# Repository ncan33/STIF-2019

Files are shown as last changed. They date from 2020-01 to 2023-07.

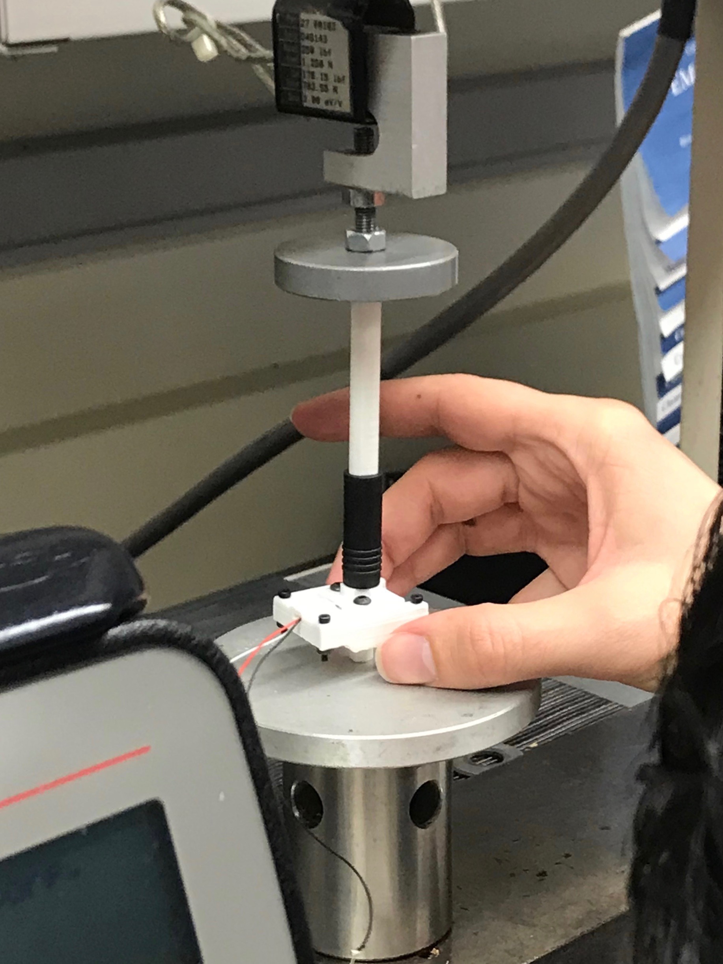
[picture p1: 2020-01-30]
data_analysis/images/calibration_on_MTS_machine.jpg

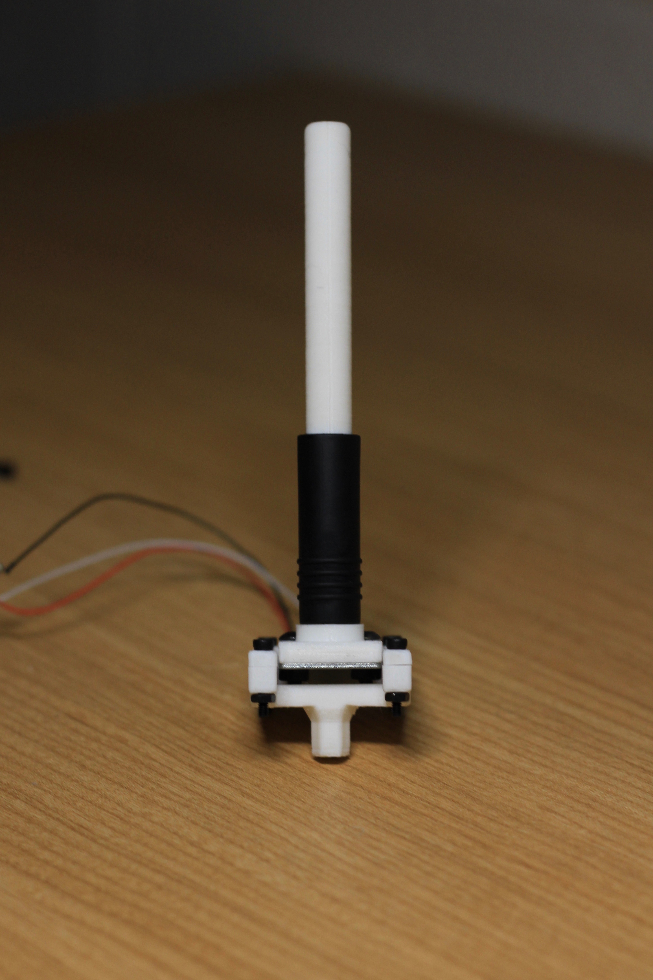
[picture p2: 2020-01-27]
visuals/IMG_4286.jpg

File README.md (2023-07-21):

# Surgery Tool with Integrated Force-gauge
This device measures the amount of force applied during controlled injury on mice. The CAD files for the 3D printed parts can be modified to achieve applicability for various surgery methods.

The strain of the aluminum beam inside the device is measured with two strain gauges. Arduino was used to control the electronics and translate incoming data from the strain gauge. Since strain is linearly correlated with the amount of force applied, the device can measure the applied force.

**[See Technical Report](https://github.com/ncan33/STIF-2019/blob/master/report.pdf)**

## Instructions
Download the Arduino IDE for Unix or Windows. In the Arduino IDE, install the [HX711 Ardunio Library](https://www.arduino.cc/reference/en/libraries/hx711-arduino-library/). Go to the `arduino_code/` and read the README. Then, go to the `arduino_code/final_code_STIF/` folder and read that README as well. Download `final_code_STIF.ino` on your computer and run it.

Our device at URMC has already been calibrated. For that specific device, you can find the digital output to force conversion in the technical report above (Equation 1). You will need to calibrate your own device, since each strain gauge is unique.

## Problem Scope
A method for measuring force values during controlled injury on mice was needed. Attempts to measure force through non-electronic means were made, however they were unsuccessful.

## Design Requirements
**Function**
* Needs to measure and store force data during surgery.
* Needs to act both as a force gauge _and_ the surgery tool.
* Will be operated by a human hand.
* Needs to measure up to 35 Newtons of force

**Reliability**
* Needs to be accurate up to research standards. The data collected by the device is intended to be published.
* Voltage output shall not be affected by ambient temperature.

**Dimensions**
* Needs to have an extruded part through which force will be applied on the mouse, which needs to satisfy the following constraints:
  * Regular hexagon
  * Short diagonal 6.15 mm
* The grip must be in the shape of the tool previously used to cause the controlled injury.

**Features**
* Must be easily operated without any special training.
* Must have an easy to use interface.
* Must have a tare function.
* Should be cleaned without damage to the device.

**Safety**
* Must not cause unwanted injuries to the mouse.
* Must not use dangerous voltages.
  
## Design Description
**Application:**
Check the [data_analysis folder](https://github.com/ncan33/STIF-2019/tree/master/data_analysis) for results acquired in the materials testing lab. An MTS machine was used to precisely apply known loads. Data collection was performed. Refer to [this document](https://github.com/ncan33/STIF-2019/blob/master/data_analysis/MATLAB_code_PDF/MTS_data_analysis_01_29_20.pdf) to access Force vs. Digital Output graph, and the 0.998 R-squared value. The graph is extremely linear and the device is proven to be functional with robust data. Repeated MTS test done for reliability-check yielded exactly the same results.

**Structure and Materials:**
All of the design requirements were met. 3D printed PLA comprises the structure of the tool due to its fine resolution and robust material properties. The strain gauge is integrated inside the surgical tool, and the device is multifunctional.

**Electronics:**
Arduino is used to control the electronics and translate incoming data from the strain gauges. The strain gauges are housed in a half-bridge load cell. Measurement range is between 0 to 98 Newtons. Measurement isn't affected by ambient temperature due to the half-bridge nature of the circuit. Two resistors were added to make a Wheatstone Bridge.

**Prototyping Cost:**
The total cost of the [materials](https://github.com/ncan33/DATAA-2019/tree/master/how_to_assemble#materials-and-tools) is under $75. Currently, 3D printing is commonly accesible at research facilities in developed countries. Thus, with the cost and tools taken into account, this is a device that is easy to assemble.

## Limitations and Future Improvements
_This project is still being developed. The first prototype is a success, however I have many ideas on how to improve it._

***Current works:***
* A housing for the electronic parts is being designed. It will be fabricated via 3D printing. I will post the .stl file in this repository.
* Means to update the strain gauge design is being researched.

***Limitations:***
* Can only measure up to 98 Newtons
* Can only be operated by a human
* Redesigning the device for other surgical applications would take hours of design and fabrication

***Future Improvements:***
* Easier adjustability
* Using a full bridge strain gauge
* Means to decrease noise in voltage detection by Arduino
* Improved grip
  * Can be made more ergonomic by allowing middle, ring, and pinky fingers to rest on an area
  * Silicon grip area is not secured to the grip
* Improved portability by removing the necessity of a computer
* Using a storage means different than the Arduino IDE serial monitor to collect data

## Creative Commons License
This device was designed, protoyped, fabricated, and assembled by Nejat Can. It is licensed under [CC Attribution-NonCommercial-ShareAlike 4.0](https://creativecommons.org/licenses/by-nc-sa/4.0/), so any research lab is allowed to use this repository to manufacture their own surgical force gauge.

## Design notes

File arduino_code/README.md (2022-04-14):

# READ THIS

***Main file*** `final_code_STIF.ino` ***uses both folders (*** `HX711_Arduino_Library` ***AND*** `final_code_STIF` ***) in order to work.***

The folder HX711_Arduino_Library needs to be placed in Arduino IDE's Library folder, or needs to be manually downloaded from the Arduino Libraries Manager located within the IDE.

`HX711_Arduino_Library` is taken from: https://github.com/bogde/HX711

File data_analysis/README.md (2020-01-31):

# DOCUMENT UNDER CONSTRUCTION

## Data Analysis
***Purpose***

***Procedure***

***Results***

The folder [CODE_MTS_test](https://github.com/ncan33/STIF-2019/blob/master/data_analysis/CODE_MTS_test/CODE_MTS_test.ino) has the

# Data Analysis
The folder [CODE_MTS_test](https://github.com/ncan33/STIF-2019/blob/master/data_analysis/CODE_MTS_test/CODE_MTS_test.ino) was the Arduino code used during the test. Data from the serial monitor was imported to Excel and raw data was analyzed in MATLAB. 

--

## Challenges
One encountered problem was the serial print had an unwanted string "Readings:". This made it harder to analyze in MATLAB, but the erase function was used to clear the cell array of unwanted strings. After the cell array was cleared of unwanted strings, it was converted to a matrix with double data type using the function str2num.

The easier approach would be to edit the Arduino code such that the 

NOT FINISHED

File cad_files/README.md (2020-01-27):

This device consists of three structural parts. STL files are to be sliced and 3D printed.

***Print these files***:
- ***[part1.stl](https://github.com/ncan33/DATAA-2019/blob/master/cad_files/DATAA_part1.stl)***
- ***[part2.stl](https://github.com/ncan33/DATAA-2019/blob/master/cad_files/DATAA_part2.stl)***
- ***[part3.stl](https://github.com/ncan33/DATAA-2019/blob/master/cad_files/DATAA_part3.stl)***

For instructions on how to manufacture and assemble the device, refer to the [how_to_assemble](https://github.com/ncan33/DATAA-2019/tree/master/how_to_assemble) folder.

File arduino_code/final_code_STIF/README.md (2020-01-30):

## Calibration
After the manufacturing & assembly process, the device must be calibrated otherwise the values will not be accurate.

**How to calibrate:**
1. Connect the Arduino to computer.
2. Apply a **known load** to the device (i.e. [perform a materials test](https://github.com/ncan33/STIF-2019/blob/master/visuals/calibration_on_MTS_machine.jpg) (recommended) or use a [precision scale](https://images-na.ssl-images-amazon.com/images/I/61YSVHc1hwL._SX425_.jpg) to apply measured loads).
3. Increase or decrease variable `calibration_factor` in the Arduino code. This will cause a direct change in the readings in the Serial Monitor.
4. When the readings match the known load, you've successfully calibrated the device.
5. (optional) Repeat with various loads ranging from 0-10.00 lb to check function.

## Tare
_The following is important. **The device is tared by resetting the Arduino**. IMPORTANT:_
* ***THE DEVICE MUST BE AT REST IN A VERTICAL POSITION WHEN THE CODE IS UPLOADED***
* ***THE DEVICE MUST BE AT REST IN A VERTICAL POSITION WHEN IT IS RESET***
* Ways to reset the device are:
  * Reupload the code, this will automatically restart the arduino
  * Hit the red reset button on the Arduino
  * Cut power supply to the Arduino, then reintroduce it
  
Tare before each usage. Tare more if needed throughout data collection.

## Measurement Unit
The measurement unit is user defined, and the default unit is pound-force.

_To define a new unit:_
1. Pick the desired force unit by editing the Arduino code
2. Recalibrate by following the steps of **How to calibrate** 

## Data Collection
To collect data, launch the Arduino IDE and connect the Arduino to your computer. Upload the code to your Arduino and open the Serial Monitor in the IDE.

## Research Application
The quality of the data is far more important for research application than convenience of usage. Therefore, for researchers the priority should be to collect good raw data, and perform data analysis afterwards. The following steps can be taken to ensure that the data is the high quality and easy to analyze using MATLAB or Excel.
* Remove units from serial output
* Use a lower calibration_factor (Recommended: 1000)
* Calibrate with a precision tool and collect multiple data points
* Refer to the [data_analysis](https://github.com/ncan33/STIF-2019/tree/master/data_analysis) for an example of data collection with this device and MATLAB analysis.
This repository has the code that satisfies these requirements. To access the code, refer to the folder [code_for_research_application](https://github.com/ncan33/STIF-2019/tree/master/arduino_code/code_for_research_application).

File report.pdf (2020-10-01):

# Device for Force Measurement in Non-Invasive Mouse ACL Injury Models: A Low-Cost and Portable Alternative

Nejat Can
Department of Biomedical Engineering University of Rochester
Rochester, NY, USA
ncan@u.rochester.edu

Abstract—Osteoarthritis and anterior cruciate ligament (ACL) injury have shown to be linked but poorly understood. Animal models are essential for understanding ACL injury, and there are a variety of models that have been developed. This study aims to introduce a new injury device that is significantly lower in cost and highly portable, suggesting ease of accessibility and better application for in situ studies. Computer-aided-design and 3D printing was used to precisely manufacture parts that encase an aluminum beam. The beam was fitted with a strain gauge, which was connected to a circuit that outputs a digital value proportional to strain. The relationship between the load on the beam and digital output was characterized by an experiment. The results indicated that digital output can confidently predict the load applied due to a linear relationship (R

2=0.9983 and
p<0.001). An in vivo non-invasive ACL injury experiment was done in accordance with our model, and results indicated that mean force at ACL rupture (14.62 N, SD = 3.00 N) and difference between males and females were consistent with previously published results. Results indicate that our model can be used to investigate ACL injury and post-traumatic osteoarthritis in mouse specimens.
Keywords—ACL injury, injury model, device, non-invasive, osteoarthritis
I. INTRODUCTION

ACL injury is common and often leads to post-traumatic osteoarthritis (PTOA). The incidence rate of ACL injury resulting in surgery and not resulting in surgery is 36.9 and 1147 per 100,000 person-years respectively [1]. Upon ACL injury, the reported incidence of PTOA is as high as 87% [2]. Mouse models are one of the most prevalent animal models used for understanding ACL injury [3]. To achieve a reliable and consistent injury model, ACL rupture can be used as an indicator of ACL injury in mice specimens.
ACL rupture can be caused by a variety of methods. One possible method is surgical ACL transection, which involves an incision through the skin and joint capsule, allowing for the ACL to be cut with another incision [4]. However, invasive models like these require surgical expertise and differ significantly than the most common cause of ACL rupture occurring in humans, which is due to acute mechanical loads on the knee. In order to counter these limitations, non-invasive models have been developed. Non-invasive models do not require surgical expertise and cause ACL rupture via mechanical loads. The scope of this paper will involve the model developed by Christiansen et al. [5] which is a reliable model resulting in no macroscopic damage to surrounding ligaments of the knee, such as PCL or MCL [4].
The model developed by Christiansen et al. counters the limitations of invasive models, however it comes with its own limitations. Load-based non-invasive models require highprecision electromagnetic materials testing machines [5,6]. Materials testing machines are expensive and immobile. The high cost makes laboratory access harder and the immobility renders in situ experiments hard to execute. To counter these limitations, a low cost and portable device has been designed in the current study, and open access .stl files and circuit diagrams have been provided on GitHub [7]. The device measures axial force by utilizing a half-bridge strain gauge integrated into a handheld tool. Device effectiveness was tested with an in vivo mouse experiment and results indicate successful emulation of the Christiansen et al. model.

II. MATERIALS AND METHODS

A. Design Requirements
In order to emulate the materials testing machine, the device must measure and store force data during ACL injury. The device must also be small and portable, as well as low-cost, in order to counter the limitations of the typical non-invasive ACL injury model. The device should require no surgical expertise to operate, as well as being easy to disinfect.
The mean compressive force at ACL rupture for mice was 10.19 N. Therefore, the device should be rated for a maximum load that will account for the load requirements. Assuming outliers exceed this average by roughly two-fold, the device must measure up to 20 N. A factor of safety for reliable force measurement was determined as F.S=2.5, rating the device at 50 N. The factor of safety for device failure was rated at 5.0, for a minimum failure load at 100 N.
The force must be measured reliably, meaning that ambient conditions such as temperature should not affect the force reading. The force must be applied via a flat smooth surface that emulates that of other non-invasive ACL injury models.

B. Design

TABLE I: TOOLS AND MATERIALS

Tool/Material | Detail/Description
3D printer | Minimum print vol.: 50x50x120 mm
Microcontroller | Arduino Uno
HX711 Load Cell Amplifier | N/A
Aluminum beam | Strain will occur on this beam
Strain gauge | Small area (≤0.4 mm² )

The device was designed with an aluminum beam with a half-bridge strain gauge integrated on it. The beam was secured to two 3D printed parts (Fig. 1) that were designed carefully to satisfy the Design Requirements. Computer-aideddesign and 3D printing were utilized for a high precision manufacturing process. This structure was coupled with a circuit which was designed to yield a digital output that is linearly proportional to the load at the the aluminum beam (Fig. 2).

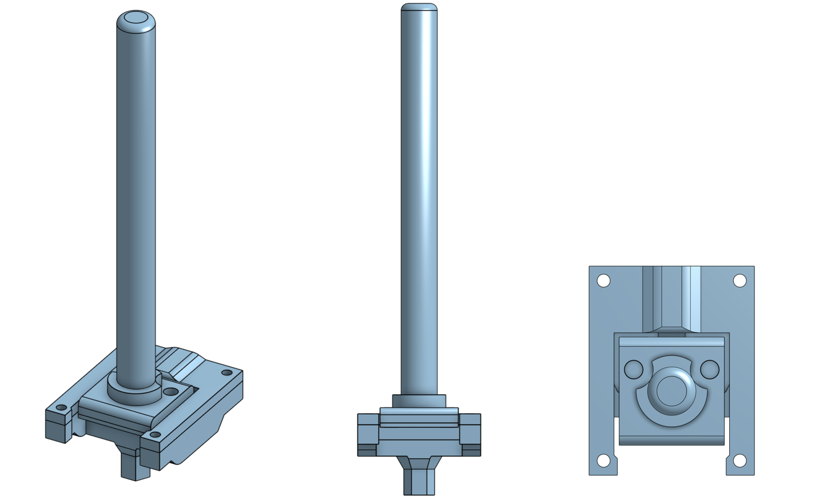
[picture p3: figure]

Fig. 1: CAD view of structure encasing the aluminum beam.

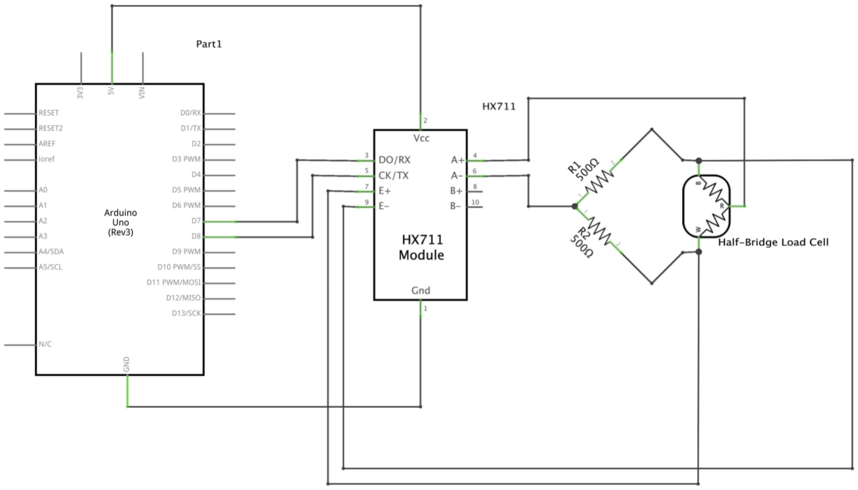
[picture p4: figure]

Fig. 2: Fritzing sketch of device circuitry with Arduino and half-bridge strain gauge

After the device was assembled, it was calibrated in order to quantify the linear relationship between digital output and load at the beam. To achieve calibration, known loads were applied to the device and the digital output was recorded over a 15 second period. This process was repeated for 12 different loads ranging from 0 to 22 N. The sampling rate of the device is 10.7 Hz, the digital output data points for each periodical load application was averaged, resulting in one digital output value per known load. A linear equation was acquired by applying simple linear regression in MATLAB via the polyfit(x,y,n) function.

F orce(x) = (0.015734 ∗ x − 1.6638) | (1)

Equation 1 indicated a very strong linear relationship (R² = 0.9983 and p<0.001). The equation yields the load at the beam for input x, that is, the digital output of the device. Fig. 3 shows the linear regression.

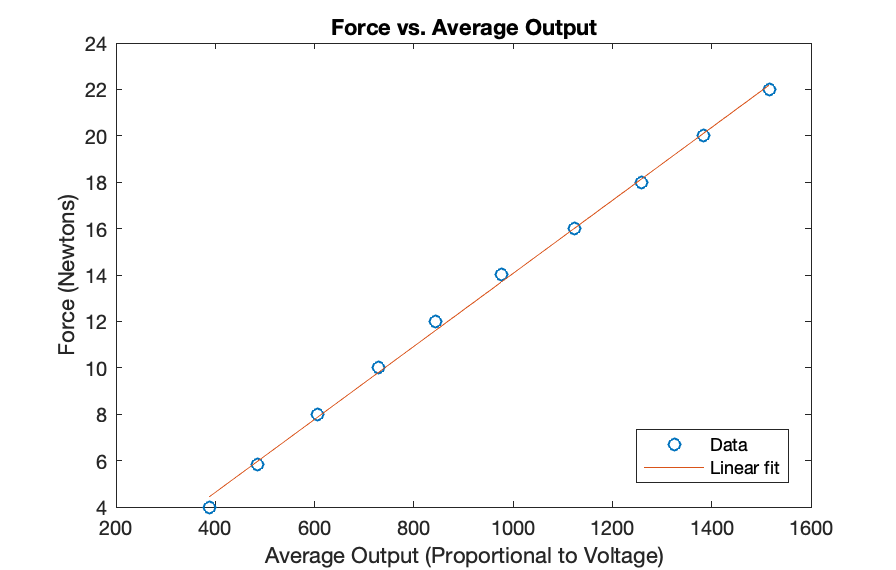
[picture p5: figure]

Fig. 3: Calibration Graph

C. In Vivo Non-Invasive ACL Injury Experiment
1) Ethics: All experiments were conducted while following animal experiment ethics rules and regulations at University of Rochester Medical Center. The current study is interested in the process of causing in vivo ACL injury, however after injury the specimens were still used for a longitudinal experiment as part of another study.
2) Method: The injury model of Christiansen et al. involves an axial compression of the lower-leg (ankle, tibia, fibula, and knee) to cause ACL rupture [5], visualized in Fig. 4(a). The current injury method emulated this model by compressing the lower-leg between the polystyrene platform and the device, visualized in Fig. 4(b).

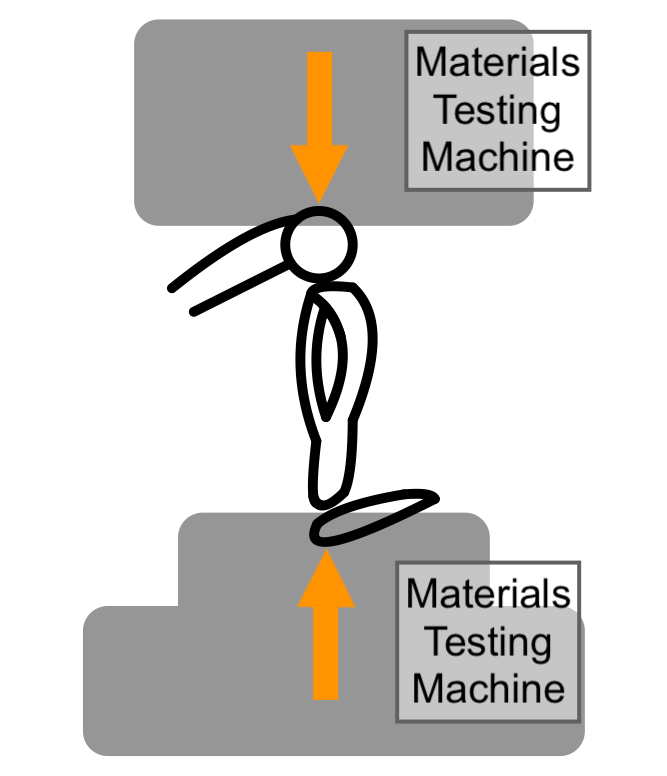
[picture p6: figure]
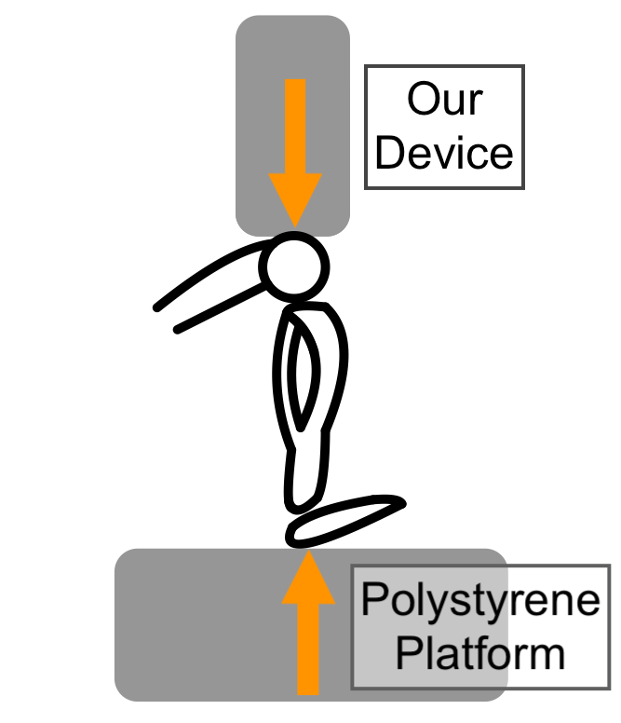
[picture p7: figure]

(a) Christiansen, et al. | (b) The current study
Fig. 4: Force delivery setup comparison

As a preliminary study, euthanized mouse specimens (n=4) were secured on a polystyrene platform with electric tape. In order to observe the integrity of the skin, the leg was rid of hair via a human-grade hair removal product. The device was aligned axially with the lower leg. Force was applied gradually at the knee axially until a ”pop” was heard or felt by the user, indicating ACL rupture. The ”pop” was heard consistently in each injury. After the injury was complete, each knee was dissected and inspected for ACL integrity and surrounding tissue damage. Table II shows that out of the 8 legs, 5 legs were injury samples and 3 legs were sham injury samples. 4 out of 5 injury samples were identified as ACL ruptured, and 1 out of 5 was inconclusive. 3 out of 5 injury samples showed no identifiable surrounding macroscopic tissue damage, and 2 out of 5 was inconclusive. The preliminary study indicated no signs for failure of effective emulation.

TABLE II: PRELIMINARY INJURY STUDY

Mouse | Leg | Injury/Sham | ACL Integrity | Surr. Damage
1 | Left Right | Injury Sham | Ruptured Intact | Absent Absent
2 | Left Right | Sham Injury | Intact Ruptured | Absent Absent
3 | Left Right | Injury Sham | Inconclusive Intact | Inconclusive Inconclusive
4 | Left Right | Injury Injury | Ruptured Inconclusive | Absent Inconclusive

Anesthetized mice (n=209) were subject to the same injury method as the euthanized mouse specimens in the preliminary study. After the injury was complete, instead of dissecting the knee, Lachman test was performed on the specimens. A positive Lachman test is evidence of ACL tear. If the Lachman test was negative, the injury attempt was repeated until the test was positive.
The Lachman test is carried out with the mouse knee bent to about 15◦
. The femur is stabilized, and the tibia is pulled forward. A steady restraint to anterior movement is considered as a normal response. Anterior displacement of proximal tibia is felt by the examiner’s thumb to determine the result of the Lachman test. Anesthesia has shown to increase the accuracy of the Lachman test [8].

III. RESULTS

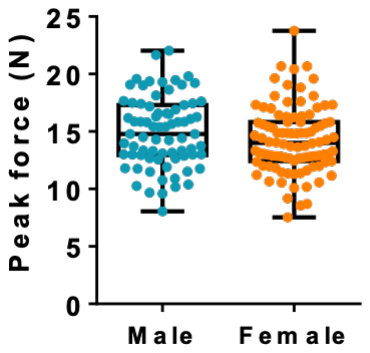
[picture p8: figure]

Fig. 5: Male vs. female load at ACL rupture

Of the 209 anesthetized specimens, 41 were excluded due to: (a) multiple attempts at ACL injury caused by negative Lachman tests, (b) unexpected behavior from the device which resulted in random graphs. The exclusion was done in order to achieve consistency. A total of 168 specimens were included. The loads at ACL rupture for specimens with multiple injury attempts had a mean within one standard deviation (SD) of the single injury attemps.
The mean load at ACL rupture was 14.62 N (σ = 3.00N) for all mice. For males and females, the mean load at ACL rupture was 14.98 N (σ = 3.06N) and 14.25 N (σ = 2.92N) respectively. Fig. 5 provides a visual contrast between males and females. Fig. 6 includes four representative graphs for the included samples. A gradual increase of force over time can be observed, which is ceased by ACL rupture at the maximum value of the curve. Table III shows the mean values of load at ACL rupture for left and right legs.

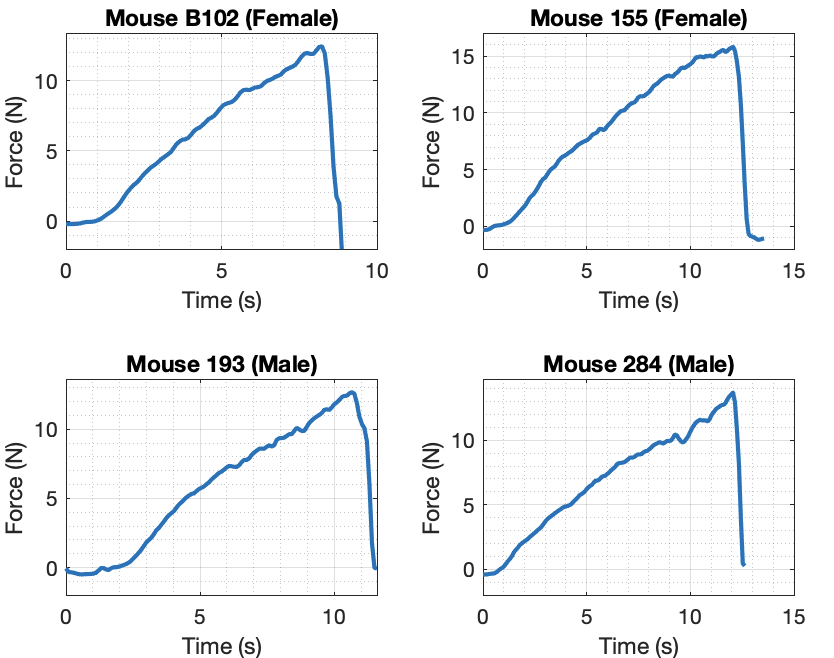
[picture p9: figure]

Fig. 6: Representative graphs for ACL injury

TABLE III: LOADS AT ACL RUPTURE

Sex | Leg | Mean (N) | SD (±)
Male | Right Left | 13.88 15.69 | 2.68 3.29
Female | Right Left | 13.88 14.56 | 2.81 3.01

IV. DISCUSSION

A. In Vivo Mouse ACL Injury Study

The calibration regression is decisively linear and the results of the in vivo injury test are highly similar to other ACL injury graphs in the literature [4]. This indicates successful emulation of the injury model developed by Christiansen et al. The mean force at ACL rupture is comparable to that of previously published results. Furthermore, previous studies have indicated no differences between male and female specimens in load at ACL rupture [4]. Similarly, in the current study, no difference between males and females was found.

B. Theory
The aluminum beam (see Materials and Methods) experiences strain when it experiences a couple loading. This results in a moment (M), which causes bending stress (σ):

σ = −

My
I

(2)

where I is the area moment of inertia and y is the distance from the neutral axis to the location of interest, which is the outer surface of the beam where two strain gauges are located. The bending stress can be converted to strain ():

= −

σ
E

(3)

for a material with modulus of elasticity E.

C. Design Parameters
1) Circuit: A Wheatstone bridge was used to quantify strain (Fig. 2). The resistance of a strain gauge is affected by ambient temperature. However, a circuit that uses a half-bridge design is not affected by variation in temperature because both resistors have equal changes in resistance, resulting in no net change in voltage.
Strain results in a small (≤ 1Ω) resistance change in the circuit with high noise and low resolution. The HX711 load cell amplifier was integrated into the circuit in order to overcome this problem, resulting in a high resolution signal with low noise.

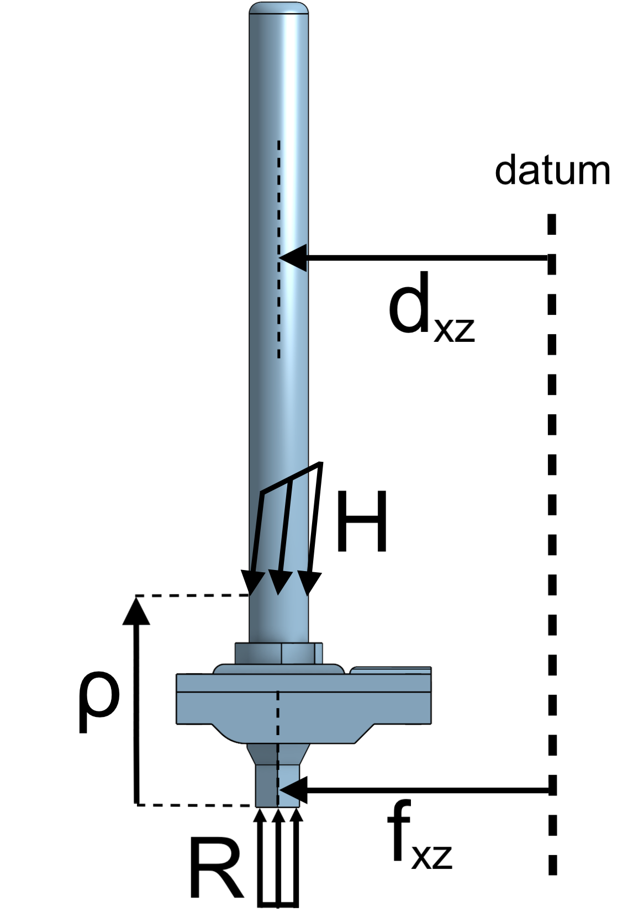
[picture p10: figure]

(a) Forces on device. | (b) Displacement between
central axis and datums
Fig. 7: Force diagrams
2) Mechanical Parts: 3D printed mechanical parts were designed to provide maximum stability during load delivery. Stability is determined by two moments. In Fig. 7(a), force H is the force applied by the hand and R is the reaction force opposing the vertical component of H. Hxy is the projection of H onto the xy-plane. Displacements (a) dxz and (b) fxz are between the vertical datum and central axis of the (a) handle and (b) extruded tip respectively. Displacement ρ originates from the reaction and terminates at the hand. Equation (4) shows that stability is maximized when ρ is minimized.

M~

1 = ~ρ × H~
xy | (4)

In Fig. 7(b), dxz (also shown in Fig. 7(a))and dyz are parallel to the xy-plane and they originate at datums and terminate at the central axis of the handle. Analogously, fxz (also shown in Fig. 7(a)) and fyz originate at the datums and terminate at the central axis of the extruded tip. Defining ~d = ~dxz + ~dyz and ~f = ~fxz + ~fyz, the displacement between the central axes of the handle and extruded tip is quantified by ∆ = ~ ~d + ~f. The second moment can be minimized by designing coincident the central axes, resulting in maximum stability.

M~

2 = ∆~ × R~ | (5)
D. Clinical Relevance

The current study has implications for the future use of in vivo ACL injury models for osteoarthritis (OA). It incorporates traumatic loading as a more realistic mode contributing to the progression of OA compared to surgical models. The model of the current study, similar to other non-invasive models, initiates joint degeneration by inducing a localized osteoarthritic joint injury through mechanical impact [9]. This is not always achievable in the surgically induced injuries (invasive). Therefore, non-invasive models are more advantageous due to better replication of human acute processes initiated by ACL rupture caused by mechanical external injuries [5].
Our model may be used to study the effects of early treatments following injuries. Additionally, the portable aspect of our model opens doors to a high variety of in situ applications. The device in our model can be characterized as a low-cost DIY alternative to other models with well-written documentation, suggesting higher accessibility compared to other non-invasive models.
E. Limitations

Although results indicated that the device is consistent and reliable, a commercial-grade materials testing machine is more reliable. Furthermore, the standard deviation for the mean ACL rupture load was higher than other studies. This may be due to imperfect emulation of other non-invasive injury models.

V. CONCLUSION

Our model is a reliable and consistent alternative to other non-invasive ACL injury models which primarily use materials testing machines. In vivo ACL injury experiments have successfully reproduced the findings of other studies. Digital output of the device has shown a decisively linear relationship to the load applied.

ACKNOWLEDGMENT

The authors would like to thank Ashley Proctor for performing the ACL injury with earlier prototypes of the device. The authors would like to thank Ahmet Selcuk Can for providing access to 3D printing equipment and ordering electronic parts. Funding sources had no involvement in study design, data acquisition, interpretation or manuscript preparation.

REFERENCES

[1] S. M. Gianotti, S. W. Marshall, P. A. Hume, and L. Bunt, “Incidence of anterior cruciate ligament injury and other knee ligament injuries: A national population-based study,” Journal of Science and Medicine in Sport, vol. 12, no. 6, pp. 622–627, Nov. 2009.
[2] N. A. Friel and C. R. Chu, “The Role of ACL Injury in the Development of Posttraumatic Knee Osteoarthritis,” Clinics in Sports Medicine, vol. 32, no. 1, pp. 1–12, Jan. 2013.
[3] M. H. Gregory, N. Capito, K. Kuroki, A. M. Stoker, J. L. Cook, and
S. L. Sherman, “A Review of Translational Animal Models for Knee Osteoarthritis,” Arthritis, vol. 2012, pp. 1–14, Dec. 2012.
[4] C. L. Blaker, C. B. Little, and E. C. Clarke, “Joint loads resulting in ACL rupture: Effects of age, sex, and body mass on injury load and mode of failure in a mouse model,” J. Orthop. Res., vol. 35, no. 8, pp. 1754–1763, Sep. 2016.
[5] B. A. Christiansen, M. J. Anderson, C. A. Lee, J. C. Williams, J. H.
N. Yik, and D. R. Haudenschild, “Musculoskeletal changes following non-invasive knee injury using a novel mouse model of post-traumatic osteoarthritis,” Osteoarthritis and Cartilage, vol. 20, no. 7, pp. 773–782, Jul. 2012.
[6] T. Maerz, M. D. Kurdziel, A. A. Davidson, K. C. Baker, K. Anderson, and H. W. T. Matthew, “Biomechanical Characterization of a Model of Noninvasive, Traumatic Anterior Cruciate Ligament Injury in the Rat,” Ann Biomed Eng, vol. 43, no. 10, pp. 2467–2476, Mar. 2015.
[7] N. Y. Can, “STIF-2019,” https://github.com/ncan33/STIF-2019
[8] H. Makhmalbaf, A. Moradi, S. Ganji, F. Omidi-Kashani, “Accuracy of lachman and anterior drawer tests for anterior cruciate ligament injuries,” Arch Bone Jt Surg, vol. 1, no. 2, pp. 94–97, Dec. 2013.
[9] B. Poulet, R. W. Hamilton, S. Shefelbine, and A. A. Pitsillides, “Characterizing a novel and adjustable noninvasive murine joint loading model,” Arthritis and Rheumatism, vol. 63, no. 1, pp. 137–147, Dec. 2010.

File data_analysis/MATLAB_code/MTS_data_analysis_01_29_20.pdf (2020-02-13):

%{

Testing done at calibration_factor = 1000;

This code does the following:
- Import raw data from force device
- Convert string to number
- Plot data and linear fit
- Calculate R-squared

Lesson learned: don't print unwanted strings in Arduino serial monitor

RESULTS: R-squared is 0.9983 so it is very strong correlation.

Note: in case the corrcoef function is giving the wrong value, maybe double
checking the R-sqared value with Excel might be a good idea.

%}

T = readtable('01_29_20_MTS_analysis.xlsx'); %import data rawdata = T.Variables; %convert table to 141x22 cell array

%readings at serial monitor as cell array
cell_array = [rawdata(:,2) rawdata(:,4) rawdata(:,6) rawdata(:,8)... rawdata(:,10) rawdata(:,12) rawdata(:,14) rawdata(:,16)... rawdata(:,18) rawdata(:,20) rawdata(:,22)];
%type rawdata in command window to inspect which row belongs to which load

pure_array = erase(cell_array,"Reading: "); %remove unwanted string from cell array
array = str2double(pure_array); %convert cell array to matrix

%variable 'array' is a matrix. make a vector for each load increment: array0 = array(:,1);
array4 = array(:,2);
array6 = array(:,3);
array8 = array(:,4);
array10 = array(:,5);
array12 = array(:,6);
array14 = array(:,7);
array16 = array(:,8);
array18 = array(:,9);
array20 = array(:,10);
array22 = array(:,11);

%DATA IS TIDY.
%BEGIN ANALYSIS:

%calculate average values: ave0 = mean(array0);
ave4 = mean(array4);
ave6 = mean(array6);
ave8 = mean(array8);
ave10 = mean(array10);
ave12 = mean(array12);
ave14 = mean(array14);
ave16 = mean(array16);
ave18 = mean(array18);
ave20 = mean(array20);
ave22 = mean(array22);

%make vectors:
ave_output =
[ave4;ave6;ave8;ave10;ave12;ave14;ave16;ave18;ave20;ave22]; force = [4;5.85;8;10;12;14;16;18;20;22];

%generate linear fit data
linear_eq = polyfit(ave_output,force,1);
linear_fit = polyval(linear_eq,ave_output);

%plot data
plot(ave_output,force,'o',ave_output,linear_fit,'-') title("Force vs. Average Output")
xlabel("Average Output (Proportional to Voltage)") ylabel("Force (Newtons)")
legend('Data','Linear fit')

%display r-squared value
disp(' ')
disp('R-squared is:')
R_matrix = corrcoef(ave_output,force); R = R_matrix(2,1);
Rsq = R^2;
disp(Rsq)

%display linear equation
eqtn = [' y=' num2str(linear_eq(1)) 'x' num2str(linear_eq(2))]; disp('Linear equation is:')
disp(eqtn)

R-squared is:
0.9983

Linear equation is:
y=0.015734x-1.6638

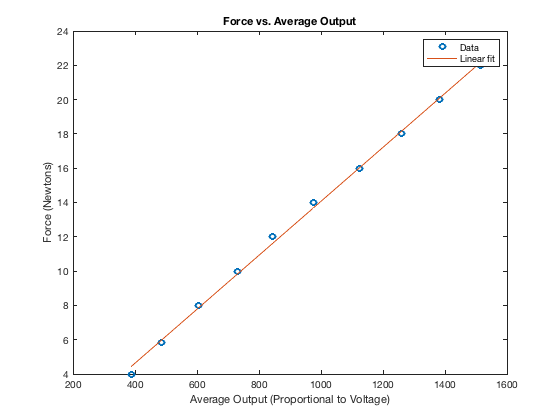
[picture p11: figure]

Published with MATLAB® R2018b

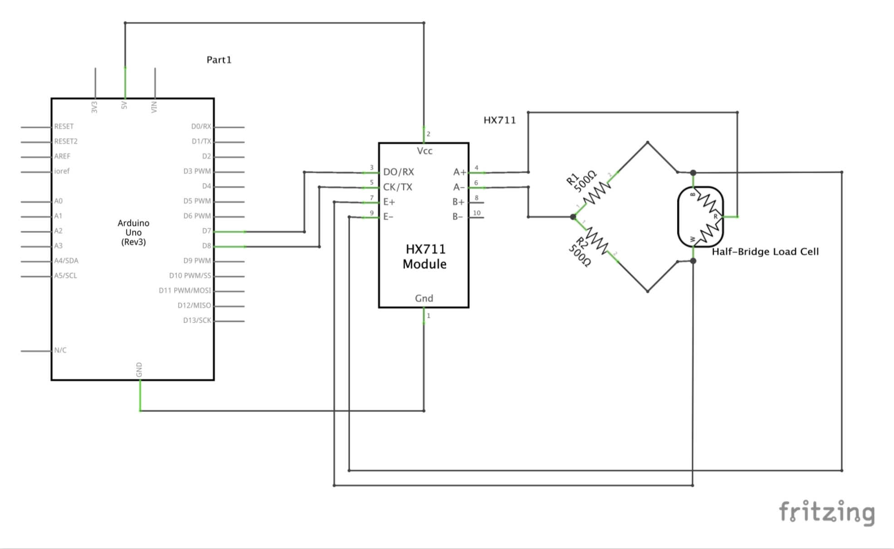
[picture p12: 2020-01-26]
circuit/circuit.png

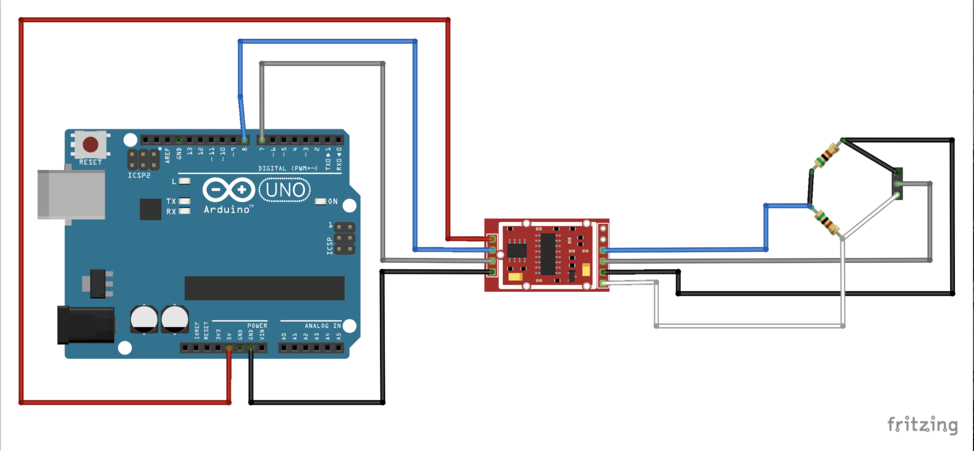
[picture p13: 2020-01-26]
circuit/circuit_visual.png

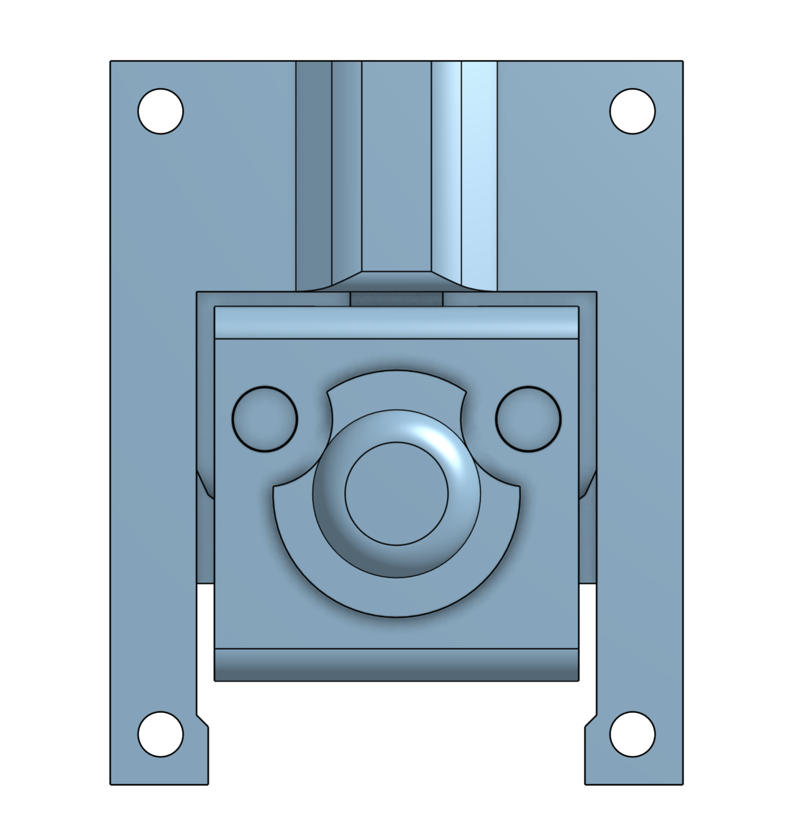
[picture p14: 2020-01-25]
visuals/top.png

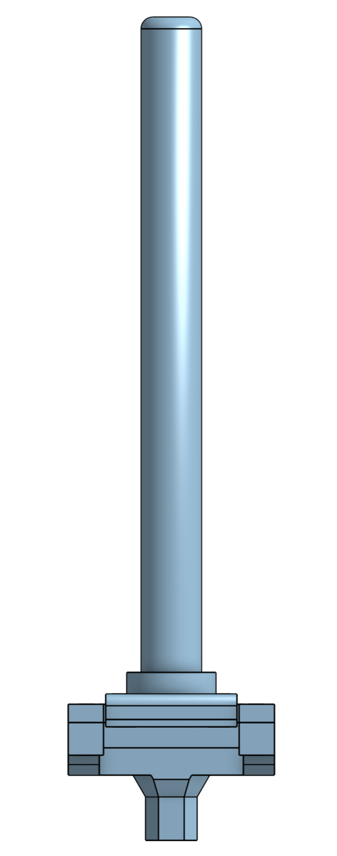
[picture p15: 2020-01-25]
visuals/front.png

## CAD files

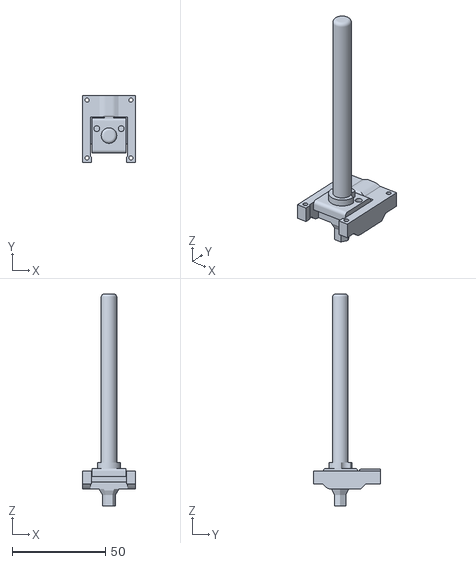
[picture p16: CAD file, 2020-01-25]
cad_files/STIF_assembly.stl
28.5 x 36.0 x 113.6

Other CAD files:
cad_files/part2.sldprt
cad_files/part3.sldprt
cad_files/part1.sldprt
cad_files/part1.stl
cad_files/part2.stl
cad_files/part3.stl

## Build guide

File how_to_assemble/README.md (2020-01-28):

# Manufacturing Guide
The purpose of this document is to provide instructions on how to manufacture and assemble S.T.I.F. (Surgery Tool with Integrated Force-gauge).

# Materials and Tools
This device is comprised of 3D printed PLA and various electronic parts.

***Tools Needed***:
* _3D printer_
  * _≤0.4 mm nozzle_
  * _Minimum print dimensions: 50x50x120 mm_
* _Soldering iron_
* _Slicer software (i.e. Ultimaker Cura, Slic3r, etc.)_

***Materials and Parts Needed:***
* _3D print material: PLA or ABS filament (PLA recommended)_
* _[uxcell 5kg Half-bridge Strain Gauge](https://www.amazon.com/dp/B07NRD5969/ref=cm_sw_em_r_mt_dp_U_WzBlEbVYCE79Q)_
* _[Arduino Kit (the following included)](https://www.amazon.com/ELEGOO-Project-Tutorial-Controller-Projects/dp/B01D8KOZF4/ref=sr_1_2_sspa?keywords=arduino+uno&qid=1580056066&s=electronics&sr=1-2-spons&psc=1&spLa=ZW5jcnlwdGVkUXVhbGlmaWVyPUEzSVAyUFRQSEtPUzlOJmVuY3J5cHRlZElkPUEwNjIyOTMzMTVYMDlFQ09NV043QSZlbmNyeXB0ZWRBZElkPUEwOTE1MDY2MzhLWVhQOVdMOVNVQiZ3aWRnZXROYW1lPXNwX2F0ZiZhY3Rpb249Y2xpY2tSZWRpcmVjdCZkb05vdExvZ0NsaWNrPXRydWU=)_
  * _Arduino Uno_
  * _Male and female jumper wires_
  * _5V power supply module_
  * _9V battery module_
* _[HX711 load cell amplifier](https://www.amazon.com/gp/product/B07MY2PBY4/ref=ppx_yo_dt_b_asin_title_o05_s00?ie=UTF8&psc=1)_
* _[Metric bolts and nuts](https://www.amazon.com/gp/product/B07HVRJW5J/ref=ppx_yo_dt_b_asin_title_o03_s00?ie=UTF8&th=1)_
  * 4 count M2x12
  * 2 count M3x8

***Skills Needed:***
* Ability to solder
* Ability to operate a 3D printer and slicer software
* Knowledge of basic circuits
* Basic knowledge of Arduino IDE software

# Manufacturing Process
After the materials and electronic parts are acquired, there are two manufacturing procedures: (1) 3D print the [cad_files](https://github.com/ncan33/DATAA-2019/tree/master/cad_files), (2) solder the [circuit](https://github.com/ncan33/DATAA-2019/tree/master/circuit).

After the circuit is soldered, protect the brittle load cell wires with heat-shrink tubes (optional).

# Assembly Process
1. Fasten `part3.stl` to the load cell using two M3x8 bolt and nut
2. Fasten `part1.stl` and `part2.stl` to the load cell using four M2x12 bolt and nut

Diagrams aren't included because it's extremely easy to assemble this device. Use the [visuals folder](https://github.com/ncan33/DATAA-2019/tree/master/visuals) as a guide during the assembly.

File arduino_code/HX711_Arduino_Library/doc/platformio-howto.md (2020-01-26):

# PlatformIO howto

https://platformio.org/

List installed platforms

    platformio platform list

List available boards

    platformio boards

Run specific build

    platformio ci --board=megaatmega2560 --lib="." examples/HX711_full_example

Run specific environment

    platformio run --environment lopy4

Build all environments

    platformio run

"Make clean" for all environments

    platformio run -t clean

Dump specific build environment

    platformio run --environment lopy4 --target envdump

See slot `CPPDEFINES`.

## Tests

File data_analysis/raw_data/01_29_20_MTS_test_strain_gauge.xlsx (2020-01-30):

Force | Output | Force | Output | Force | Output | Force | Output | Force | Output | Force | Output | Force | Output | Force | Output | Force | Output | Force | Output | Force | Output
0 N | Force values: | 4 N | Reading: 393.3 | 5.85 N | Reading: 490.2 | 8 N | Reading: 605.1 | 10 N | Reading: 736.8 | 12 N | Reading: 851.3 | 14 N | Reading: 978.8 | 16 N | Reading: 1136.7 | 18 N | Reading: 1259.3 | 20 N | Reading: 1385.2 | 22 N | Reading: 1515.0
 | Reading: 17.9 |  | Reading: 393.0 |  | Reading: 490.1 |  | Reading: 605.0 |  | Reading: 736.7 |  | Reading: 850.9 |  | Reading: 978.7 |  | Reading: 1136.2 |  | Reading: 1259.3 |  | Reading: 1384.9 |  | Reading: 1515.1
 | Reading: 17.9 |  | Reading: 392.5 |  | Reading: 490.0 |  | Reading: 604.9 |  | Reading: 736.5 |  | Reading: 850.7 |  | Reading: 978.6 |  | Reading: 1133.7 |  | Reading: 1259.2 |  | Reading: 1384.9 |  | Reading: 1515.2
 | Reading: 18.3 |  | Reading: 392.3 |  | Reading: 489.9 |  | Reading: 604.9 |  | Reading: 736.0 |  | Reading: 850.6 |  | Reading: 978.5 |  | Reading: 1129.8 |  | Reading: 1259.2 |  | Reading: 1385.0 |  | Reading: 1515.2
 | Reading: 19.2 |  | Reading: 392.2 |  | Reading: 490.0 |  | Reading: 605.1 |  | Reading: 736.0 |  | Reading: 850.2 |  | Reading: 978.5 |  | Reading: 1125.8 |  | Reading: 1258.9 |  | Reading: 1384.7 |  | Reading: 1515.3
 | Reading: 20.1 |  | Reading: 392.3 |  | Reading: 489.8 |  | Reading: 605.1 |  | Reading: 736.0 |  | Reading: 850.0 |  | Reading: 978.5 |  | Reading: 1122.6 |  | Reading: 1258.7 |  | Reading: 1384.6 |  | Reading: 1515.2
 | Reading: 21.4 |  | Reading: 392.4 |  | Reading: 490.0 |  | Reading: 605.2 |  | Reading: 736.0 |  | Reading: 849.9 |  | Reading: 978.4 |  | Reading: 1121.6 |  | Reading: 1258.6 |  | Reading: 1384.6 |  | Reading: 1515.2
 | Reading: 22.5 |  | Reading: 392.5 |  | Reading: 489.9 |  | Reading: 605.2 |  | Reading: 736.1 |  | Reading: 849.6 |  | Reading: 978.5 |  | Reading: 1121.3 |  | Reading: 1258.9 |  | Reading: 1384.6 |  | Reading: 1515.5
 | Reading: 23.1 |  | Reading: 392.6 |  | Reading: 489.9 |  | Reading: 605.2 |  | Reading: 736.2 |  | Reading: 849.5 |  | Reading: 978.5 |  | Reading: 1121.5 |  | Reading: 1259.3 |  | Reading: 1384.8 |  | Reading: 1515.4
 | Reading: 26.7 |  | Reading: 392.5 |  | Reading: 489.8 |  | Reading: 605.1 |  | Reading: 736.2 |  | Reading: 849.6 |  | Reading: 978.5 |  | Reading: 1121.4 |  | Reading: 1259.1 |  | Reading: 1384.8 |  | Reading: 1515.4
 | Reading: 29.8 |  | Reading: 392.6 |  | Reading: 489.7 |  | Reading: 604.9 |  | Reading: 736.4 |  | Reading: 849.7 |  | Reading: 978.7 |  | Reading: 1121.5 |  | Reading: 1258.9 |  | Reading: 1385.0 |  | Reading: 1515.4
 | Reading: 23.0 |  | Reading: 392.7 |  | Reading: 489.6 |  | Reading: 604.8 |  | Reading: 736.3 |  | Reading: 849.7 |  | Reading: 978.8 |  | Reading: 1121.4 |  | Reading: 1258.7 |  | Reading: 1385.1 |  | Reading: 1515.4
 | Reading: 20.4 |  | Reading: 392.6 |  | Reading: 489.6 |  | Reading: 604.9 |  | Reading: 736.1 |  | Reading: 849.5 |  | Reading: 978.6 |  | Reading: 1121.3 |  | Reading: 1258.9 |  | Reading: 1385.0 |  | Reading: 1515.5
 | Reading: 18.7 |  | Reading: 392.5 |  | Reading: 489.4 |  | Reading: 605.3 |  | Reading: 736.1 |  | Reading: 849.4 |  | Reading: 978.4 |  | Reading: 1121.1 |  | Reading: 1259.2 |  | Reading: 1384.8 |  | Reading: 1515.3
 | Reading: 17.6 |  | Reading: 392.4 |  | Reading: 489.4 |  | Reading: 605.3 |  | Reading: 736.1 |  | Reading: 849.3 |  | Reading: 978.2 |  | Reading: 1121.1 |  | Reading: 1259.4 |  | Reading: 1384.9 |  | Reading: 1515.3
 | Reading: 14.9 |  | Reading: 392.5 |  | Reading: 489.5 |  | Reading: 605.5 |  | Reading: 736.1 |  | Reading: 849.2 |  | Reading: 978.1 |  | Reading: 1121.0 |  | Reading: 1259.4 |  | Reading: 1385.0 |  | Reading: 1515.3
 | Reading: 10.9 |  | Reading: 392.5 |  | Reading: 489.5 |  | Reading: 605.6 |  | Reading: 736.2 |  | Reading: 849.1 |  | Reading: 978.0 |  | Reading: 1121.0 |  | Reading: 1259.4 |  | Reading: 1385.0 |  | Reading: 1515.2
 | Reading: 10.6 |  | Reading: 392.5 |  | Reading: 489.2 |  | Reading: 605.7 |  | Reading: 736.0 |  | Reading: 849.2 |  | Reading: 978.1 |  | Reading: 1120.9 |  | Reading: 1259.5 |  | Reading: 1384.9 |  | Reading: 1515.0
 | Reading: 10.8 |  | Reading: 392.4 |  | Reading: 488.8 |  | Reading: 605.8 |  | Reading: 735.4 |  | Reading: 849.2 |  | Reading: 978.2 |  | Reading: 1120.9 |  | Reading: 1259.6 |  | Reading: 1384.6 |  | Reading: 1515.0
 | Reading: 9.4 |  | Reading: 392.3 |  | Reading: 488.5 |  | Reading: 606.0 |  | Reading: 735.2 |  | Reading: 848.9 |  | Reading: 978.2 |  | Reading: 1121.1 |  | Reading: 1259.5 |  | Reading: 1384.8 |  | Reading: 1515.1
 | Reading: 8.0 |  | Reading: 392.1 |  | Reading: 488.3 |  | Reading: 606.1 |  | Reading: 735.1 |  | Reading: 848.4 |  | Reading: 978.3 |  | Reading: 1121.0 |  | Reading: 1259.2 |  | Reading: 1384.9 |  | Reading: 1515.2
 | Reading: 9.4 |  | Reading: 392.2 |  | Reading: 488.2 |  | Reading: 606.1 |  | Reading: 735.2 |  | Reading: 848.0 |  | Reading: 978.2 |  | Reading: 1120.9 |  | Reading: 1259.1 |  | Reading: 1384.8 |  | Reading: 1515.2
 | Reading: 11.9 |  | Reading: 392.3 |  | Reading: 488.0 |  | Reading: 606.1 |  | Reading: 735.2 |  | Reading: 847.8 |  | Reading: 978.0 |  | Reading: 1120.7 |  | Reading: 1259.1 |  | Reading: 1384.5 |  | Reading: 1515.4
 | Reading: 14.1 |  | Reading: 392.2 |  | Reading: 487.9 |  | Reading: 606.1 |  | Reading: 735.2 |  | Reading: 847.5 |  | Reading: 978.0 |  | Reading: 1120.7 |  | Reading: 1259.1 |  | Reading: 1384.5 |  | Reading: 1515.5
 | Reading: 16.9 |  | Reading: 392.1 |  | Reading: 487.8 |  | Reading: 606.1 |  | Reading: 735.1 |  | Reading: 847.4 |  | Reading: 978.2 |  | Reading: 1120.9 |  | Reading: 1259.0 |  | Reading: 1384.6 |  | Reading: 1515.3
 | Reading: 19.6 |  | Reading: 391.8 |  | Reading: 487.7 |  | Reading: 606.0 |  | Reading: 735.2 |  | Reading: 847.5 |  | Reading: 978.1 |  | Reading: 1121.4 |  | Reading: 1258.9 |  | Reading: 1385.0 |  | Reading: 1515.3
 | Reading: 21.5 |  | Reading: 391.8 |  | Reading: 487.4 |  | Reading: 605.9 |  | Reading: 735.2 |  | Reading: 847.6 |  | Reading: 978.1 |  | Reading: 1121.7 |  | Reading: 1258.9 |  | Reading: 1385.0 |  | Reading: 1515.2
 | Reading: 23.2 |  | Reading: 391.8 |  | Reading: 487.4 |  | Reading: 606.0 |  | Reading: 735.1 |  | Reading: 847.9 |  | Reading: 978.2 |  | Reading: 1121.7 |  | Reading: 1259.0 |  | Reading: 1384.9 |  | Reading: 1514.9
 | Reading: 23.9 |  | Reading: 391.7 |  | Reading: 487.5 |  | Reading: 606.2 |  | Reading: 735.1 |  | Reading: 847.6 |  | Reading: 978.3 |  | Reading: 1121.8 |  | Reading: 1259.3 |  | Reading: 1384.9 |  | Reading: 1514.8
 | Reading: 22.5 |  | Reading: 391.8 |  | Reading: 487.3 |  | Reading: 606.3 |  | Reading: 735.3 |  | Reading: 847.0 |  | Reading: 978.1 |  | Reading: 1122.0 |  | Reading: 1259.6 |  | Reading: 1385.0 |  | Reading: 1514.6
 | Reading: 19.7 |  | Reading: 391.9 |  | Reading: 487.3 |  | Reading: 606.0 |  | Reading: 735.5 |  | Reading: 846.4 |  | Reading: 978.4 |  | Reading: 1121.7 |  | Reading: 1259.7 |  | Reading: 1384.7 |  | Reading: 1514.7
 | Reading: 17.7 |  | Reading: 391.6 |  | Reading: 487.2 |  | Reading: 606.0 |  | Reading: 735.4 |  | Reading: 846.1 |  | Reading: 978.3 |  | Reading: 1121.6 |  | Reading: 1259.3 |  | Reading: 1384.6 |  | Reading: 1515.1
 | Reading: 16.6 |  | Reading: 391.6 |  | Reading: 487.2 |  | Reading: 606.0 |  | Reading: 735.3 |  | Reading: 846.0 |  | Reading: 978.1 |  | Reading: 1121.6 |  | Reading: 1259.5 |  | Reading: 1384.8 |  | Reading: 1515.1
 | Reading: 16.1 |  | Reading: 392.1 |  | Reading: 487.0 |  | Reading: 606.0 |  | Reading: 735.4 |  | Reading: 845.9 |  | Reading: 978.0 |  | Reading: 1121.6 |  | Reading: 1259.4 |  | Reading: 1384.7 |  | Reading: 1514.8
 | Reading: 15.9 |  | Reading: 392.1 |  | Reading: 486.7 |  | Reading: 606.3 |  | Reading: 735.4 |  | Reading: 845.9 |  | Reading: 978.1 |  | Reading: 1121.8 |  | Reading: 1259.5 |  | Reading: 1384.5 |  | Reading: 1514.7
 | Reading: 15.3 |  | Reading: 392.0 |  | Reading: 486.8 |  | Reading: 606.6 |  | Reading: 735.4 |  | Reading: 845.8 |  | Reading: 978.2 |  | Reading: 1122.1 |  | Reading: 1259.4 |  | Reading: 1384.4 |  | Reading: 1514.7
 | Reading: 14.5 |  | Reading: 392.1 |  | Reading: 487.0 |  | Reading: 606.7 |  | Reading: 735.3 |  | Reading: 845.4 |  | Reading: 978.2 |  | Reading: 1122.2 |  | Reading: 1259.2 |  | Reading: 1384.4 |  | Reading: 1514.7
 | Reading: 11.4 |  | Reading: 392.3 |  | Reading: 487.2 |  | Reading: 606.4 |  | Reading: 735.1 |  | Reading: 845.1 |  | Reading: 978.2 |  | Reading: 1122.0 |  | Reading: 1259.1 |  | Reading: 1384.4 |  | Reading: 1514.7
 | Reading: 7.9 |  | Reading: 392.3 |  | Reading: 487.3 |  | Reading: 606.0 |  | Reading: 735.2 |  | Reading: 845.0 |  | Reading: 978.2 |  | Reading: 1122.1 |  | Reading: 1259.3 |  | Reading: 1384.7 |  | Reading: 1514.8
 | Reading: 7.2 |  | Reading: 392.2 |  | Reading: 487.0 |  | Reading: 605.8 |  | Reading: 735.4 |  | Reading: 845.1 |  | Reading: 978.2 |  | Reading: 1122.0 |  | Reading: 1259.4 |  | Reading: 1384.8 |  | Reading: 1514.9
 | Reading: 7.6 |  | Reading: 392.0 |  | Reading: 486.9 |  | Reading: 605.8 |  | Reading: 735.5 |  | Reading: 845.2 |  | Reading: 978.2 |  | Reading: 1122.0 |  | Reading: 1259.4 |  | Reading: 1384.6 |  | Reading: 1514.9
 | Reading: 8.5 |  | Reading: 391.6 |  | Reading: 486.7 |  | Reading: 605.9 |  | Reading: 735.4 |  | Reading: 845.1 |  | Reading: 978.2 |  | Reading: 1121.9 |  | Reading: 1259.4 |  | Reading: 1384.4 |  | Reading: 1514.8
 | Reading: 9.5 |  | Reading: 391.5 |  | Reading: 486.5 |  | Reading: 605.7 |  | Reading: 735.7 |  | Reading: 844.9 |  | Reading: 978.5 |  | Reading: 1121.8 |  | Reading: 1259.4 |  | Reading: 1384.5 |  | Reading: 1514.8
 | Reading: 9.7 |  | Reading: 391.5 |  | Reading: 486.6 |  | Reading: 605.7 |  | Reading: 735.8 |  | Reading: 844.7 |  | Reading: 978.8 |  | Reading: 1121.8 |  | Reading: 1259.4 |  | Reading: 1384.6 |  | Reading: 1515.0
 | Reading: 9.9 |  | Reading: 391.6 |  | Reading: 486.6 |  | Reading: 605.3 |  | Reading: 735.7 |  | Reading: 844.6 |  | Reading: 978.7 |  | Reading: 1121.6 |  | Reading: 1259.2 |  | Reading: 1384.6 |  | Reading: 1515.1
 | Reading: 10.4 |  | Reading: 391.7 |  | Reading: 486.4 |  | Reading: 604.9 |  | Reading: 735.6 |  | Reading: 844.5 |  | Reading: 978.9 |  | Reading: 1121.7 |  | Reading: 1259.1 |  | Reading: 1384.4 |  | Reading: 1515.1
 | Reading: 11.0 |  | Reading: 391.5 |  | Reading: 486.3 |  | Reading: 605.1 |  | Reading: 735.4 |  | Reading: 844.6 |  | Reading: 978.7 |  | Reading: 1121.7 |  | Reading: 1259.2 |  | Reading: 1384.5 |  | Reading: 1515.1
 | Reading: 11.3 |  | Reading: 391.6 |  | Reading: 486.3 |  | Reading: 605.2 |  | Reading: 735.1 |  | Reading: 844.6 |  | Reading: 978.7 |  | Reading: 1121.7 |  | Reading: 1259.2 |  | Reading: 1384.4 |  | Reading: 1515.1
 | Reading: 11.9 |  | Reading: 391.5 |  | Reading: 486.4 |  | Reading: 605.4 |  | Reading: 735.0 |  | Reading: 844.8 |  | Reading: 978.7 |  | Reading: 1121.7 |  | Reading: 1259.3 |  | Reading: 1384.5 |  | Reading: 1515.1
 | Reading: 12.4 |  | Reading: 391.6 |  | Reading: 486.4 |  | Reading: 605.6 |  | Reading: 735.0 |  | Reading: 845.0 |  | Reading: 978.7 |  | Reading: 1121.6 |  | Reading: 1259.3 |  | Reading: 1384.5 |  | Reading: 1515.1
 | Reading: 12.4 |  | Reading: 391.9 |  | Reading: 486.3 |  | Reading: 605.7 |  | Reading: 735.1 |  | Reading: 844.9 |  | Reading: 978.5 |  | Reading: 1121.5 |  | Reading: 1259.4 |  | Reading: 1384.4 |  | Reading: 1515.0
 | Reading: 11.8 |  | Reading: 391.8 |  | Reading: 486.2 |  | Reading: 606.0 |  | Reading: 735.1 |  | Reading: 845.1 |  | Reading: 978.5 |  | Reading: 1121.5 |  | Reading: 1259.5 |  | Reading: 1384.4 |  | Reading: 1515.1
 | Reading: 9.6 |  | Reading: 391.7 |  | Reading: 486.1 |  | Reading: 606.3 |  | Reading: 734.9 |  | Reading: 847.3 |  | Reading: 978.4 |  | Reading: 1121.6 |  | Reading: 1259.4 |  | Reading: 1384.5 |  | Reading: 1515.3
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
